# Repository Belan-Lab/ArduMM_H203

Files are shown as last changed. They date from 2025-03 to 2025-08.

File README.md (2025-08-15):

ArduMM Controllers for Lab 203
===================================

[Arduino](https://micro-manager.org/Arduino) device adatper for Micromanager.

# PhotonMaker
[Manual](https://www.nanotoolsbio.com/_files/ugd/c3bee4_bcea98b0b7ba4d2aa8f413fe1c6c36ac.pdf)

Standard [DB15 color code](https://cdn.graftek.com/system/files/14147/original/785605-01.pdf)

### TTL trigger IN
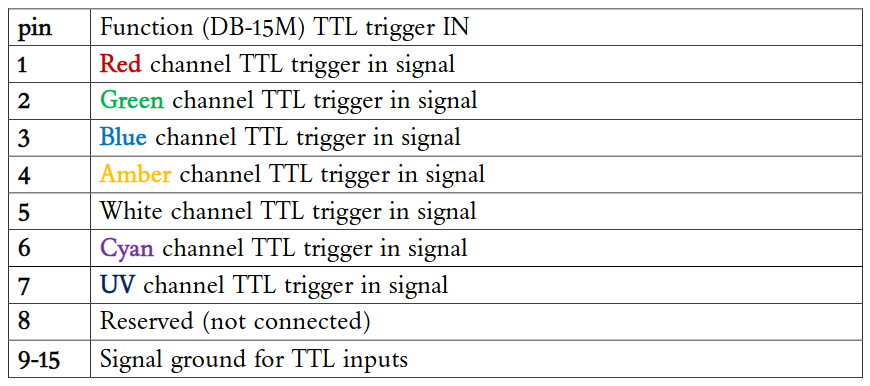
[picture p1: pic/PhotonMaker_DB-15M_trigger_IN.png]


## PhotonMaker setup

PhotonMaker control with 3 ArduMM pins and  8-channel multiplexer ([74HC4051D](https://arduino.ua/prod6234-modyl-analogovogo-myltipleksora-74hc4051d?srsltid=AfmBOopynwxA2QRn2_hYkh429Qz9YPAdudDBhhF_F8vhxPwqT6g5fnpo)).

### ArduMM digital IO

| PIN  | Bit  | Decimal Value ON | Use  |
| :--: | :--: | :--------------: | :--: |
|  8   |  0   |        1         | N/A  |
|  9   |  1   |        2         | BNC  |
|  10  |  2   |        4         | BNC  |
|  11  |  3   |        8         | S2   |
|  12  |  4   |        16        | S1   |
|  13  |  5   |        32        | S0   |

### System config

| IN S0 | IN S1 | IN S2 | ArduMM Switch-State | Channel ON | PhotonMaker Channel | PhotonMaker DB15 PIN |
| :---: | :---: | :---: | :-----------------: | :--------: | :-----------------: | :------------------: |
|   L   |   L   |   L   |          0          |     Y0     |          -          |          -           |
|   H   |   L   |   L   |         32          |     Y1     |     UV (398 nm)     |          7           |
|   L   |   H   |   L   |         16          |     Y2     |    Blue (452 nm)    |          3           |
|   H   |   H   |   L   |         48          |     Y3     |    Cyan (500 nm)    |          6           |
|   L   |   L   |   H   |          8          |     Y4     |   Green (515 nm)    |          2           |
|   H   |   L   |   H   |         40          |     Y5     |   Amber (601 nm)    |          4           |
|   L   |   H   |   H   |         24          |     Y6     |    Red (638 nm)     |          1           |
|   H   |   H   |   H   |         56          |     Y7     |        White        |          5           |

_Note: Y0 stay unused because it is HIGH when all arduino pins are LOW._

# Lynx

Lumencor Lynx (__Lynx 4-GEH-FA__, serial No. 7918, power supply 24V / 1.7A DC) - 4 colour OEM modification of the Lumencor Aura II.

### Light path
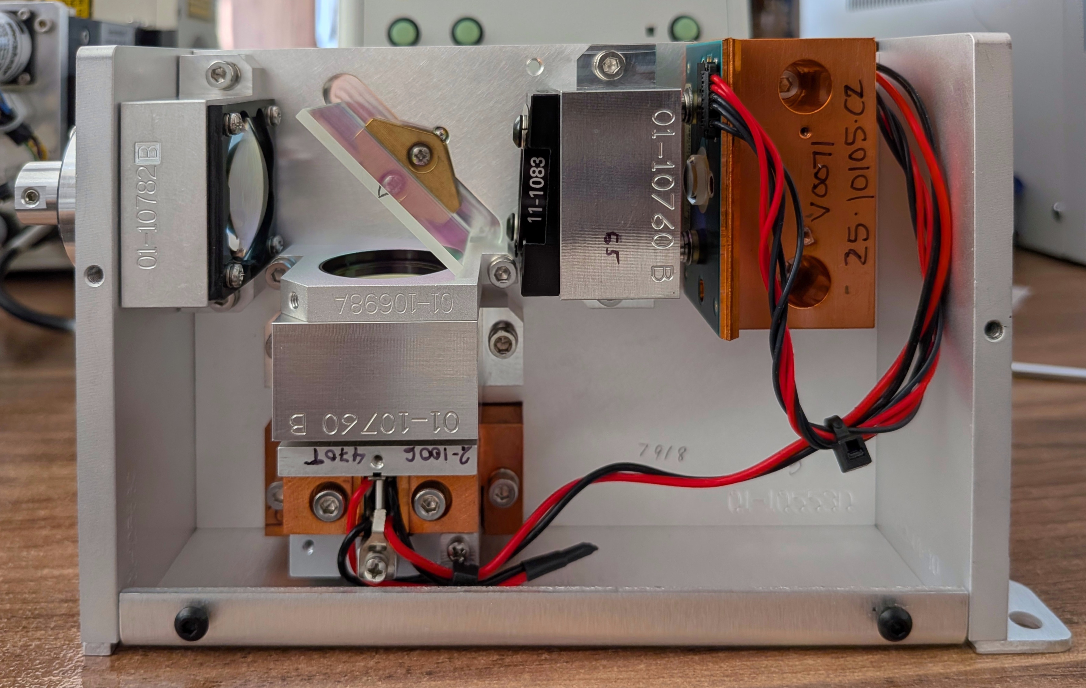
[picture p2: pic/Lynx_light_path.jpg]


Top filter - 390-475-632 (11-1083)
Bottom filter - 542/33-25

### Wavelength
|Ch. name| Installed filters mid **λ** | Lynx DB15 IN | Approx. power at the Olympus U-LLG150 output |
|:-:|:-:|:-:|:-:|
|Violet (405 nm)|390 nm|3|24 mW|
|Cyan (488 nm)  |475 nm|12|23 mW|
|Green (540 nm) |542 nm|2|12 mW|
|Red (640 nm)   |632 nm|1|14 mW|

_Note: it's estimated channels wavelength, exact filters parameters are unknown._

### TTL trigger IN
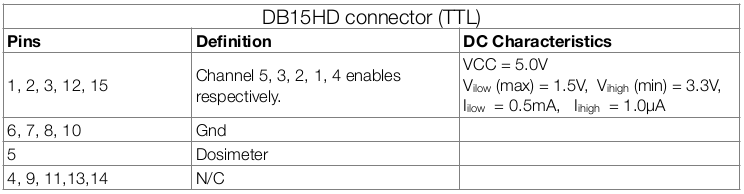
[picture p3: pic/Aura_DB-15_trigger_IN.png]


_Note: Lynx's DB15M pin-out is the same with Lumencor Aura II_

## Lynx setup

### ArduMM digital IO

| Arduino PIN | Bit  | Decimal Value ON | Use    | Lynx DB15 PIN |
| :--: | :--: | :--------------: | :----: | :-----: |
|  8   |  0   |        1         | Violet |3|
|  9   |  1   |        2         | Cyan   |12|
|  10  |  2   |        4         | Green  |2|
|  11  |  3   |        8         | Red    |1|
|  12  |  4   |        16        | BNC    |n/a|
|  13  |  5   |        32        | BNC    |n/a|

### Liquid light guide coupling

Coupling with proprietary 3 mm liquid light guide [Olympus U-LLG150](https://evidentscientific.com/en/products/light-sources/u-lgps).

|Original LLG port| LLG port model|
|:-:|:-:|
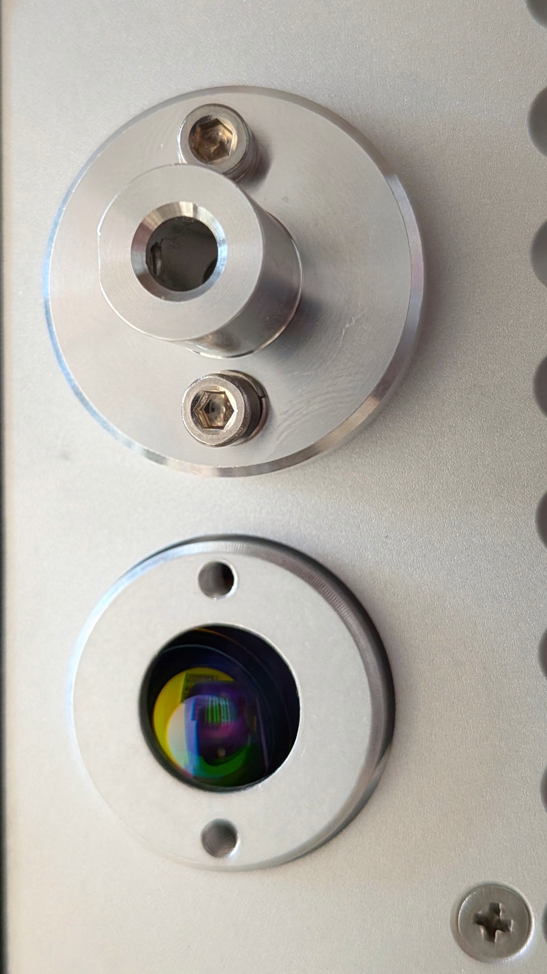
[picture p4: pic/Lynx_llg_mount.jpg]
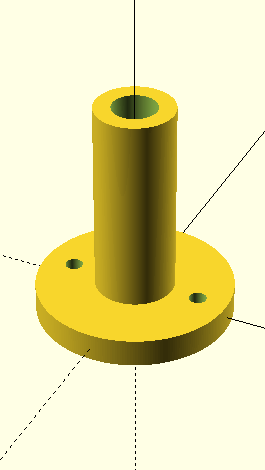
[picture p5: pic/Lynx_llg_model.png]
|||

## STL Models
The following models from open sources were used in this project:
- [OpenSCAD Arduino Mounting library](https://github.com/kellyegan/OpenSCAD-Arduino-Mounting-Library)

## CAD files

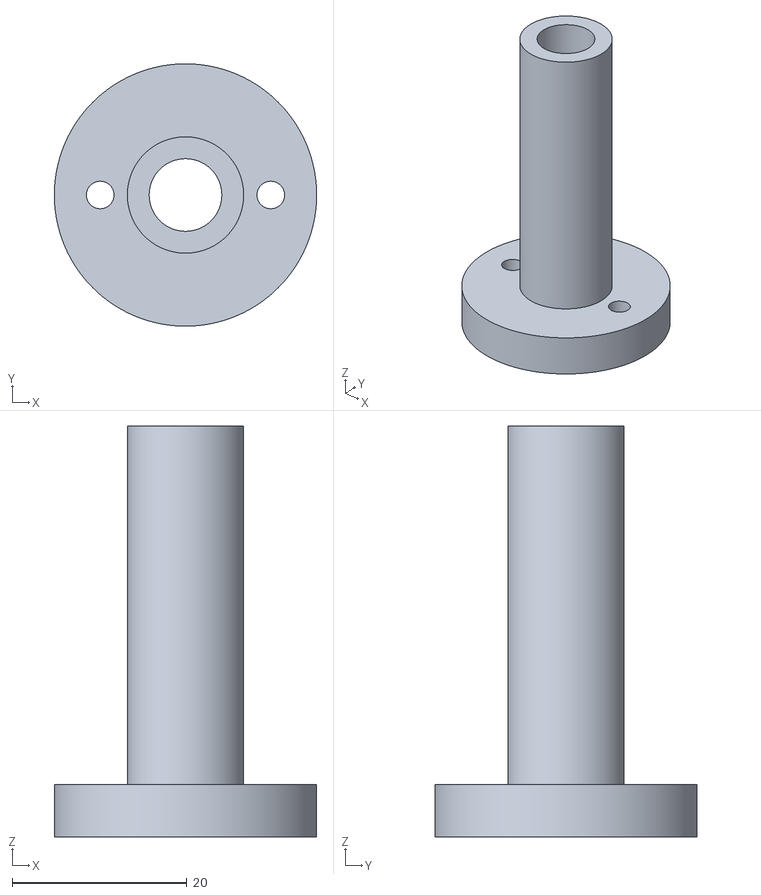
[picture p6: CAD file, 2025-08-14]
3D/Lynx_LLG/Lynx_LLG_v1.stl
30.0 x 30.0 x 47.0

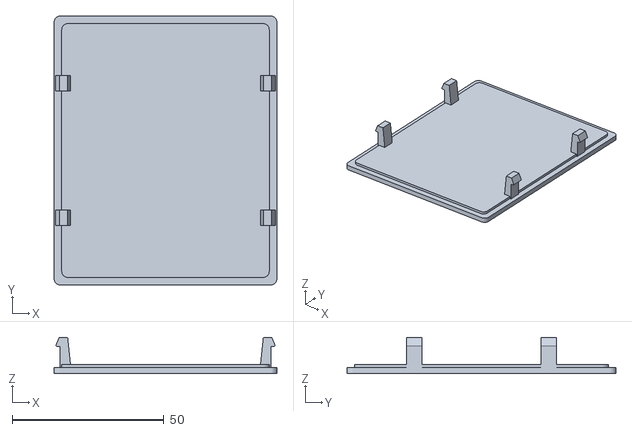
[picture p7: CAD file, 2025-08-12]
3D/PhotonMaker_UNO_case/UNO_lid.stl
73.3 x 88.6 x 12.0

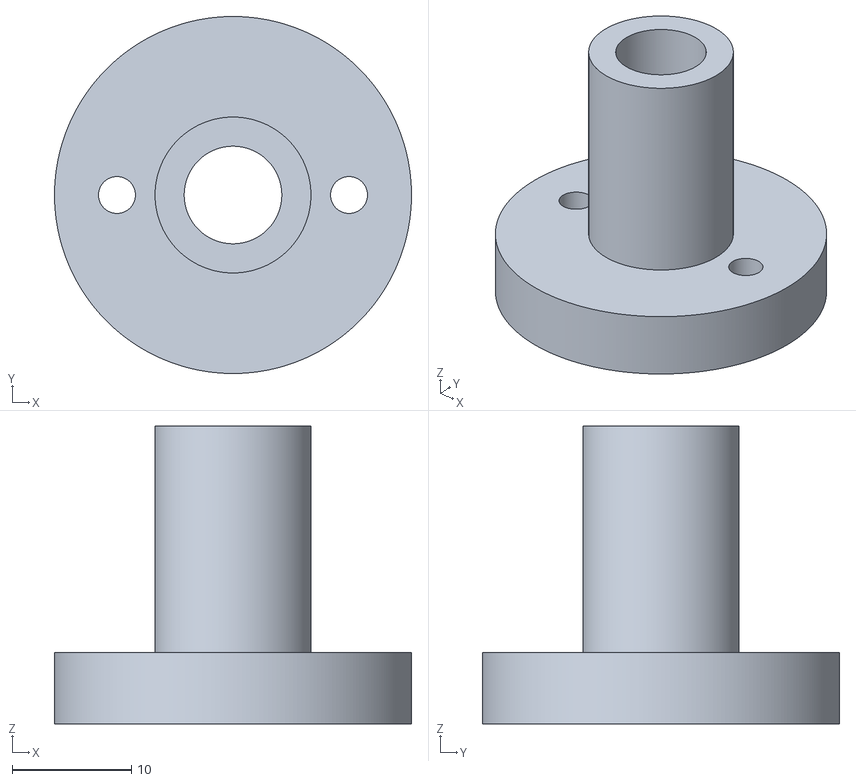
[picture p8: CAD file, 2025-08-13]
3D/Lynx_LLG/Lynx_LLG_v0.stl
30.0 x 30.0 x 25.0

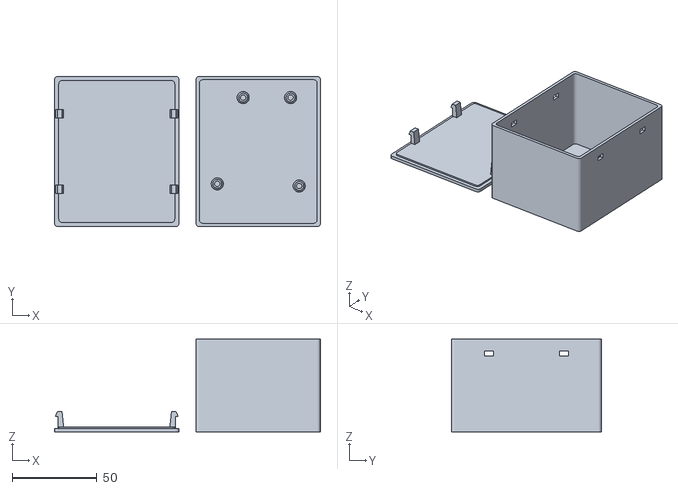
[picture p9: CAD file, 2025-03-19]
3D/PhotonMaker_UNO_case/UNO_case.stl
156.7 x 88.6 x 54.7

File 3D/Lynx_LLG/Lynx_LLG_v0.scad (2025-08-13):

FDM_offset = 0.1;

llg_d = 8.2;

base_d = 30;
base_h = 6;

tube_d = 13;
tube_h = 25;

hole_d = 3;
hole_pos = (22.45 - 2.95)/2;


module lynx_llg (){
    difference(){
        // body
        union(){
            cylinder(h = base_h, d = base_d, center = true, $fn = 256);
            translate([0,0,tube_h/2 - base_h/2])
                cylinder(h = tube_h, d = tube_d + FDM_offset,
                         center = true, $fn = 256);
        }
        
        // hole for llg
        cylinder(h = tube_h*3, d = llg_d, center = true, $fn = 256);
        
        // mounting holes
        translate([hole_pos,0,0])
            cylinder(h = base_h*2, d = hole_d + FDM_offset,
                     center = true, $fn = 256);
        translate([-hole_pos,0,0])
            cylinder(h = base_h*2, d = hole_d + FDM_offset,
                     center = true, $fn = 256);
    }
}

lynx_llg();

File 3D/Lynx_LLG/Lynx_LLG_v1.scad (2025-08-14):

FDM_offset = 0.15;

llg_d = 8.3;

base_d = 30;
base_h = 6;

tube_d = 13;
tube_h = 47;

hole_d = 3;
hole_pos = (22.45 - 2.95)/2;


module lynx_llg (){
    difference(){
        // body
        union(){
            cylinder(h = base_h, d = base_d, center = true, $fn = 256);
            translate([0,0,tube_h/2 - base_h/2])
                cylinder(h = tube_h, d = tube_d + FDM_offset*2,
                         center = true, $fn = 256);
        }
        
        // hole for llg
        cylinder(h = tube_h*3, d = llg_d, center = true, $fn = 256);
        
        // mounting holes
        translate([hole_pos,0,0])
            cylinder(h = base_h*2, d = hole_d + FDM_offset,
                     center = true, $fn = 256);
        translate([-hole_pos,0,0])
            cylinder(h = base_h*2, d = hole_d + FDM_offset,
                     center = true, $fn = 256);
    }
}

lynx_llg();

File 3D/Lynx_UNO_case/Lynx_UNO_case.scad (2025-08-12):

include </home/wisstock/.local/share/OpenSCAD/libraries/OpenSCAD-Arduino-Mounting-Library/arduino.scad>


bnc_d = 8;


    enclosure(UNO,
              wall = 2,
              offset = 5,
              heightExtension = 20,
              cornerRadius = 20,
              mountType = TAPHOLE);  // PIN


rotate([0,180,0])
translate([30,0,-2])
     
enclosureLid(UNO,
             wall = 2, offset = 5,
             cornerRadius = 20,
             ventHoles = true);

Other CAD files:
3D/PhotonMaker_UNO_case/UNO_case.scad

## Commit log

2025-03-19 19.03.2025: init commit
    [UNO_case.scad, UNO_case.stl]
2025-08-12 12.08.2025: ass Lynx
    [Lynx_LLG_v0.scad, Lynx_UNO_case.scad, UNO_case.scad, UNO_case.stl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]
2025-08-13 13.08.2025: U-LLG150 port v0
    [Lynx_LLG_v0.scad, Lynx_LLG_v0.stl]
